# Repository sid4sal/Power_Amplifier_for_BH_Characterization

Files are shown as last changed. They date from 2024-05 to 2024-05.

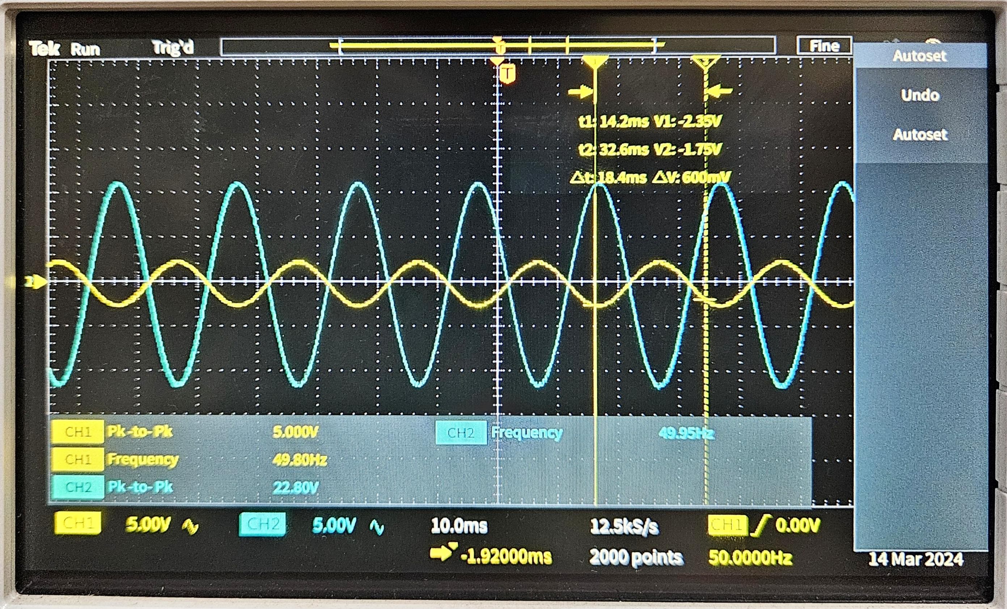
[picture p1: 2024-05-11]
Experiment Results/Vin (ch1) vs Vout (ch2) of the power amplifier.jpeg

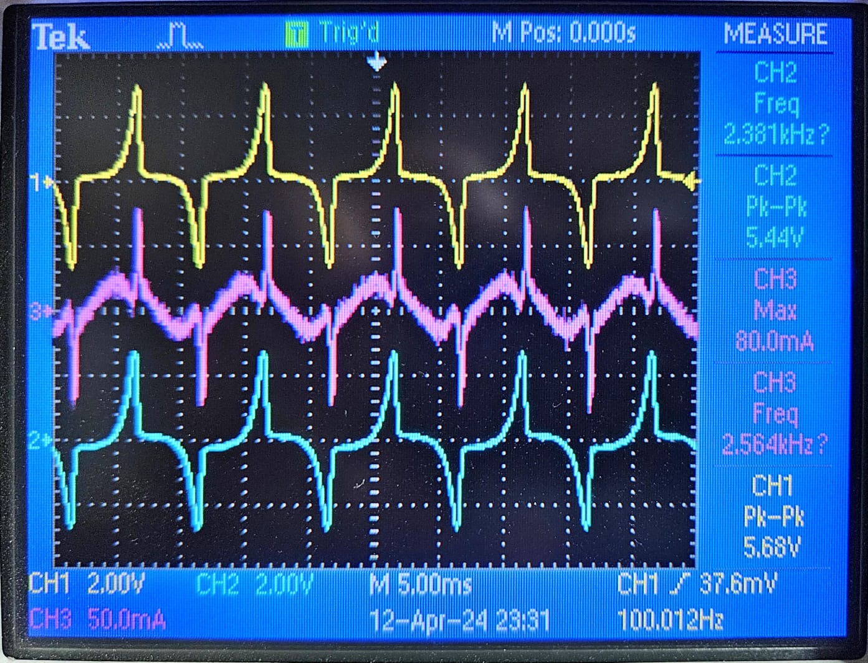
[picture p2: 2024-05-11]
Experiment Results/Primary current (ch3), primary voltage (ch2) and secondary voltage (ch1) at 500hz, 3vpp.jpeg

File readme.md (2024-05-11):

# Design and Implementation of High Bandwidth Power Amplifier for B-H Characterization of Magnetic Materials

## Project Overview

The High Bandwidth Power Amplifier is a device for magnetic materials engineers to obtain B-H characterization of magnetic materials at low as well as high frequencies. It is a transformer-less multi-stage direct-coupled linear power amplifier for the characterization of magnetic cores at various frequencies.

The amplifier operates from 50 Hz to 250 kHz with a gain of approximately 4.6 (13.2 dB). It can handle an input power voltage up to ±60 V, allowing the reference signal to be given up to 12-13 V. The current rating of the amplifier is up to 2.5-3 A (continuous).

The user manual and all the required files can be found at this repo.

## Folder Descriptions

- *B-H_curve_plotting_MatLab*: Contains MATLAB files for plotting the simulated B-H curve of the toroid.
  
- *CAD_Outer_Casing_Design*: Includes the design of the outer casing in JPEG format.
  
- *Circuit_Design_and_simulation_results*: Contains the circuit diagrams, stages, and frequency response simulations in both KiCad and Proteus formats. It also includes the PCB design and 3D view, along with potential improvements.
  
- *Demo_and_Experiment_Videos*: Holds videos demonstrating the initial testing of the breadboard circuit, testing of the amplifier on the toroid core, and PCB testing.
  
- *Experiment Results*: Contains experimental results like B-H characteristic data, observed frequency response with load, and primary and secondary voltages at different frequencies.
  
- *Frequency_Response_Observed_vs_Simulated*: Compares the observed and simulated frequency responses in KiCad and Proteus.
  
- *PCB_Design_and_Circuit_Simulation_KiCad*: Placeholder for the KiCad files related to PCB design and circuit simulation.
  
- *Simulation_Proteus*: Placeholder for the Proteus simulation files.

## Additional Documents

- *Circuit_Diagram.png*: Circuit diagram of the power amplifier.
  
- *PCB.jpeg* & *PCB2.jpeg*: Images of the PCB design.
  
- *Project_Problem_Statement.docx*: Detailed problem statement of the project.
  
- *Toroidal_core_design_and_calculation.pdf*: Design and calculations related to the toroidal core.
  
- *Toroid_Core_Detailed_Calculations.pdf*: Detailed calculations for the toroidal core.
  
- *User Manual for Power Amplifier.pdf*: User manual for operating the power amplifier.

Feel free to reach out to me for any clarifications or further details. my contact details can be found inside the user manual.

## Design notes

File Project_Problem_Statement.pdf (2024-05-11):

# Design and Implementation of High Bandwidth Power Amplifier for B-H Characterization of Magnetic Materials

By

## Siddhesh Sali

(18D070030 - IIT Bombay, Electrical Engineering)

Under Guidance of

## Prof. S V Kulkarni

(Dept. of Electrical Engineering IIT Bombay)

## Prof. Shiladri Chakraborty

(Dept. of Electrical Engineering IIT Bombay)

## Prof. Siddharth Tallur

(Dept. of Electrical Engineering IIT Bombay)

Brief description of what the students are required to build in this project (application, performance requirements and constraints)

The experimental characterization of the magnetic core material at low as well as high frequencies is required as machines and converters operate at a wide range of frequencies. For this, power amplifiers having wide bandwidth, high voltage, and current gains, along with low output offset are needed. In this project, students will build high-bandwidth voltage and current amplifiers for B-H characterization of magnetic materials. The setup will look similar to the one shown in Ref 1.

Key technical and user specifications

The designed power amplifier should be capable of characterizing a ferrite core material using the ring-specimen method up to a peak flux density of 0.3 T for a wide frequency range from 50 Hz to 10 kHz.

Deliverable expected

A review of conventional topologies and the new amplifier design should be given. The experimental results of the proposed voltage and current amplifiers and the closed-loop power amplifier need to be presented. Experimental waveforms of secondary induced voltage, core flux-linkage, and primary coil current should be shown. The students should give inputs to extend the frequency range from 10 kHz to 50 kHz.

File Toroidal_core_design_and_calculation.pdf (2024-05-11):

### 2024 date

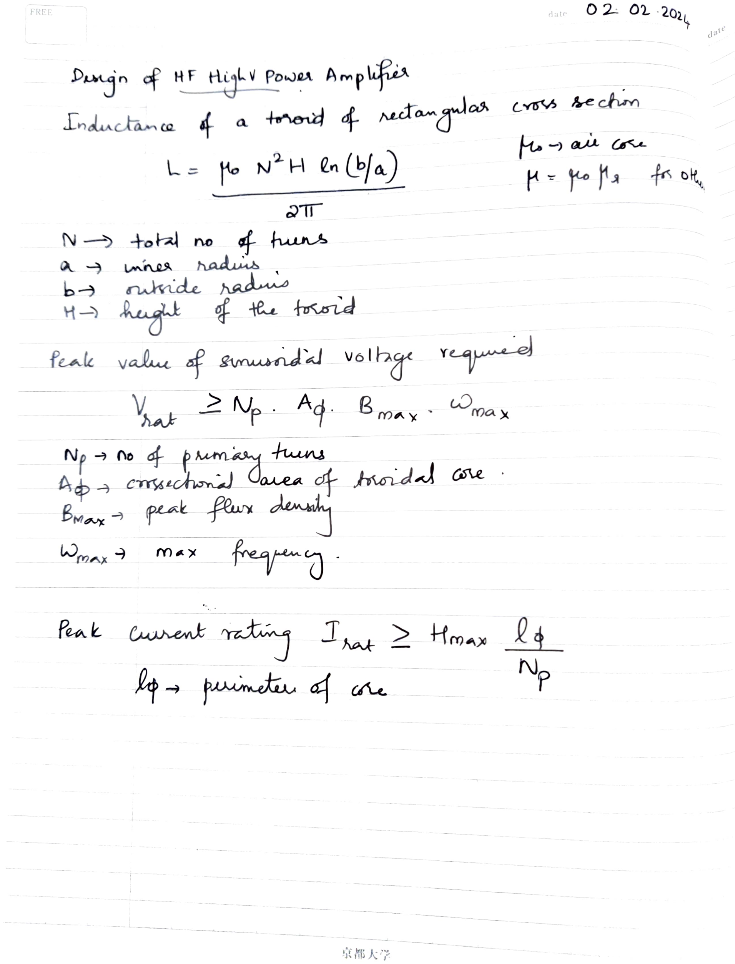
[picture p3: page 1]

FREE
PoJea Amplfhes
Inductama 4 a tohod ¢ etamga

Ntotal no

b’

Le fo NH en (b/a)

Buas

nnes hadis
ride hadis

feak vale f sinndad volage

cnsechnl

max

Peak Crent

Ad. Bmay
tuns

Boav Wa

reqe

date

CYoS bechn

### dependng on aailaki liy

## (A vailaLe at eementl4)

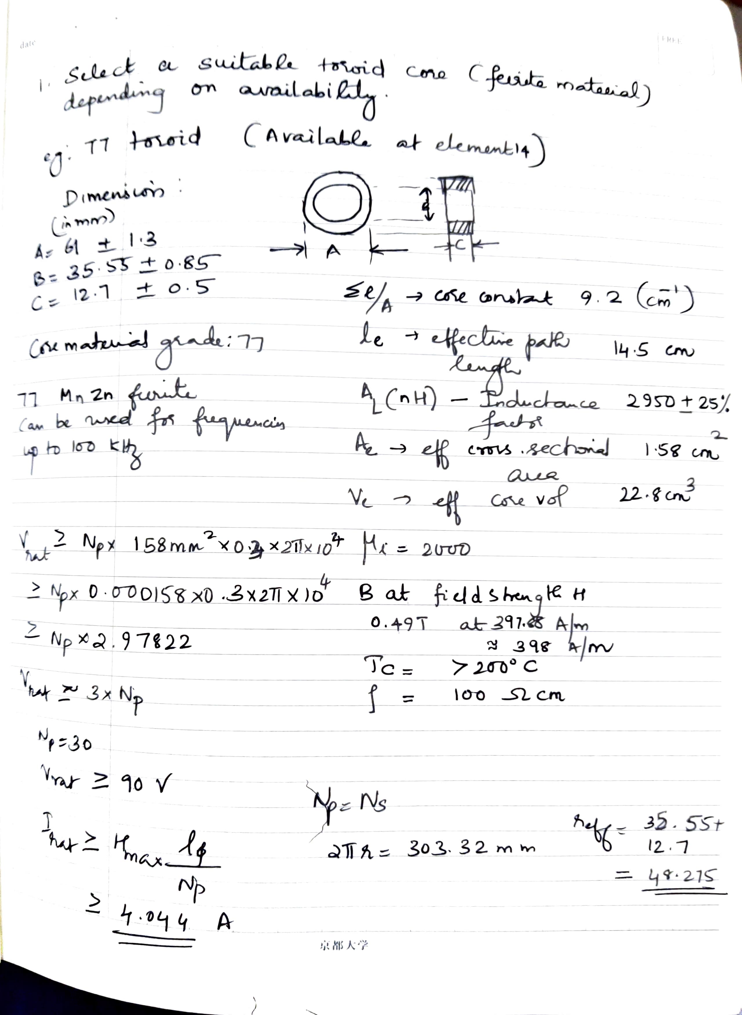
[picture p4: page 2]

date

1: T7 toroid

Dimenin
(à mm)
A 6 + l3
B: 35 S3 to-85

t

71 Mn 2n fit

2 Np xa.9 7622

30

4.o4 4 A

A
S’ cse outat 9.2 (cm')

A

Ve
158 mmxox21x 10T = 200D

’

## Cfeita tasil)

0.49T
f

CUS Bechi

B at fddshenge H

Cse vof

at 297.8 Afon

|o0 | S cm
1A | 303. 32 m m

2950t 25,

2

35. 55t
I2.7

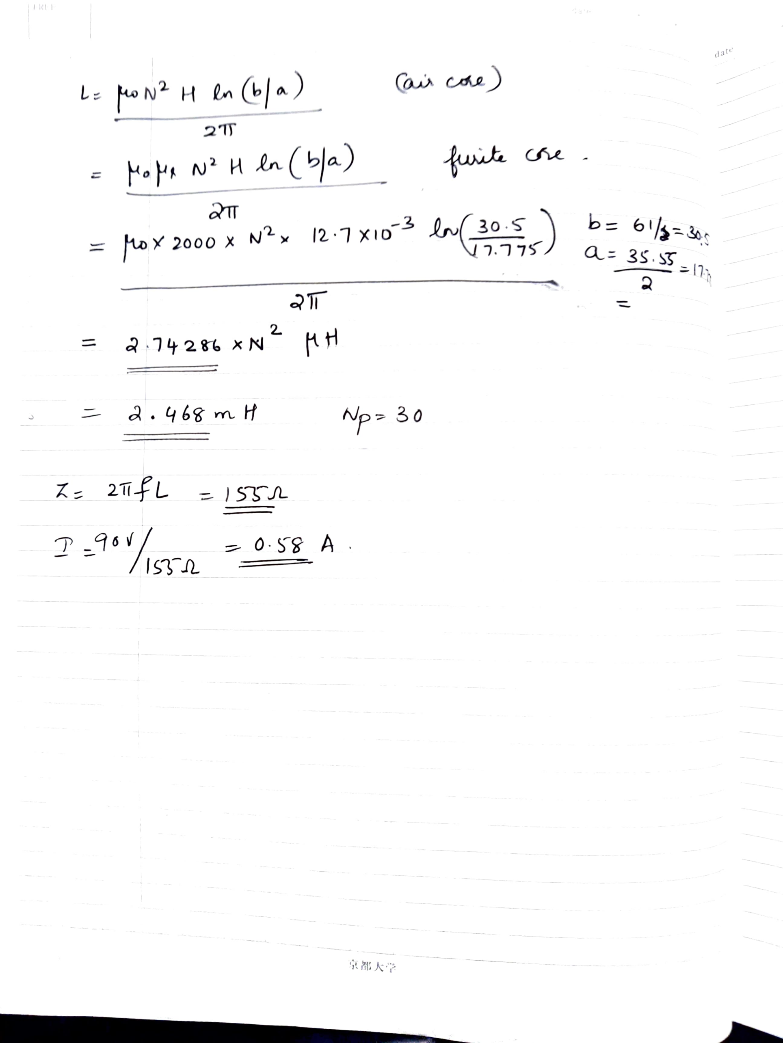
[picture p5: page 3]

Le hoN H ln

21)

= ox 2000 X N?

a. 468 m H

/a)

2

Cais cae)

2-1x103 la30s b= 6'

0.SS A

30

az 3S.SS.

date'

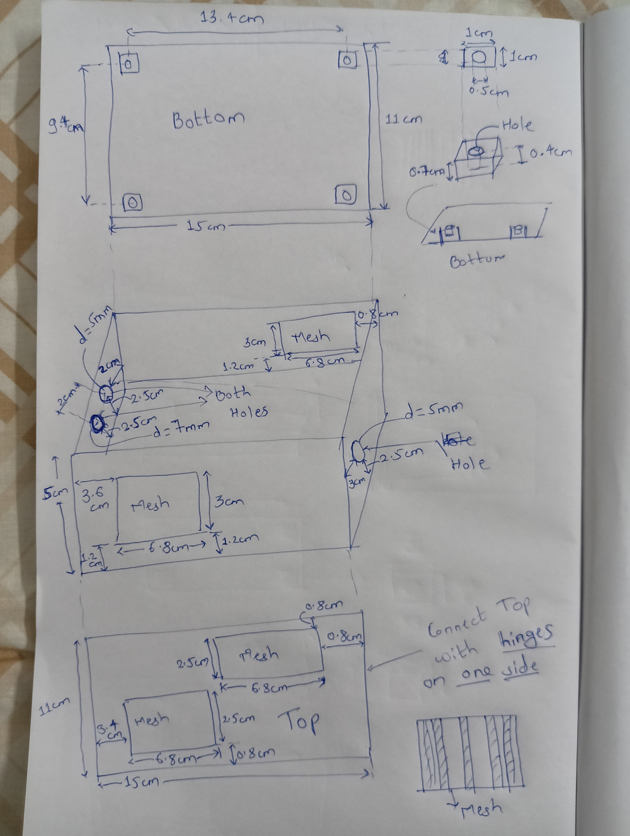
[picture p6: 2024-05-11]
CAD_Outer_Casing_Design/Outer_Casing.jpeg

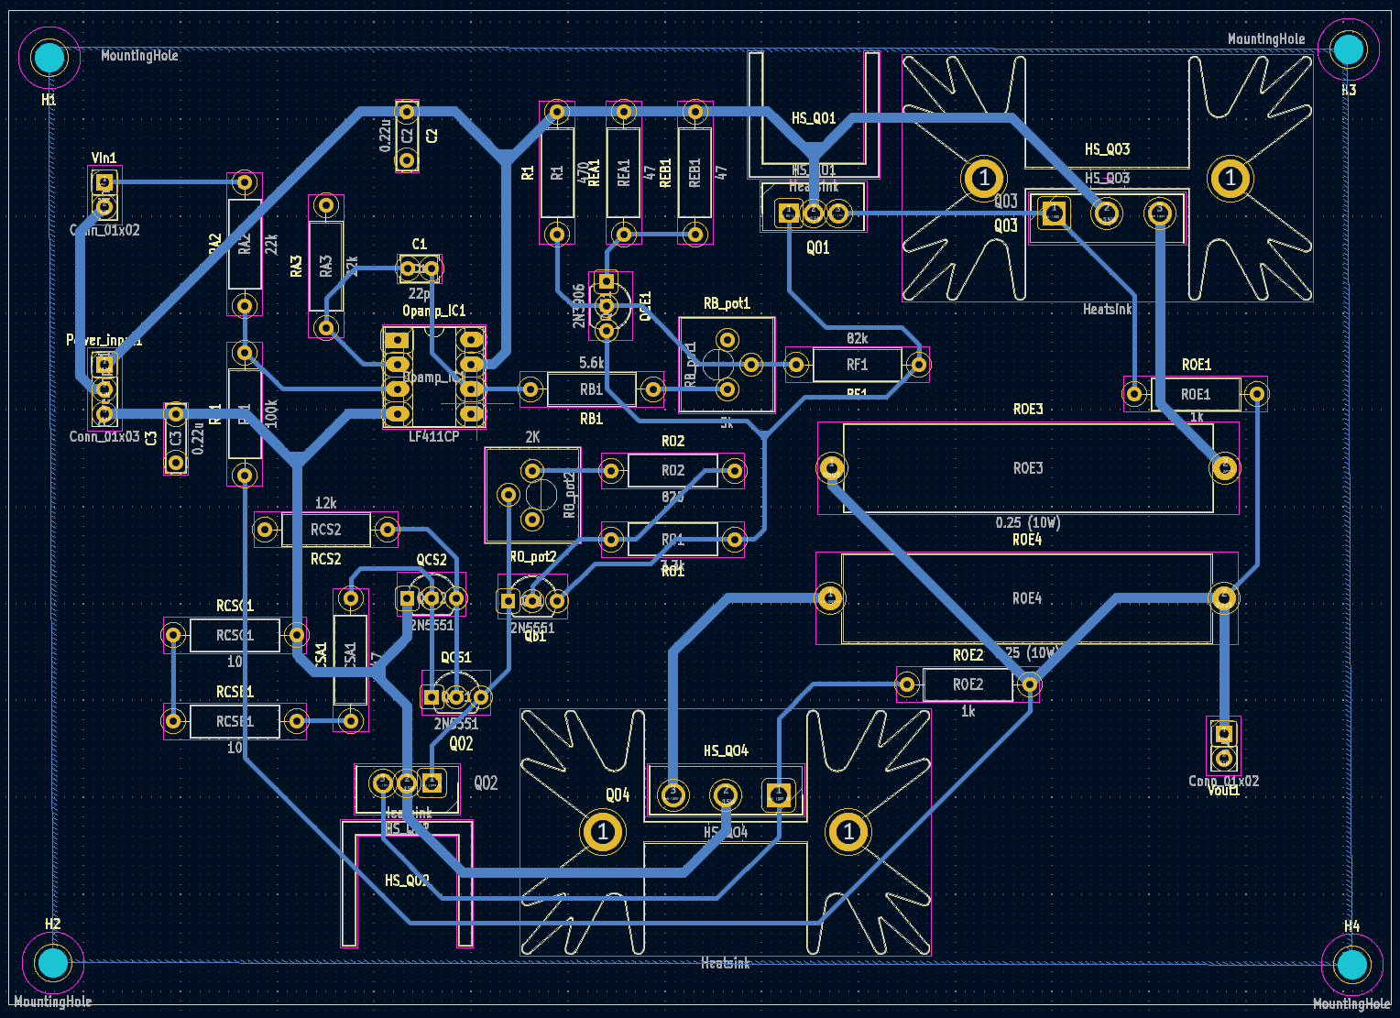
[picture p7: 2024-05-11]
Circuit_Design_and_simulation_results/PCB_Design.png

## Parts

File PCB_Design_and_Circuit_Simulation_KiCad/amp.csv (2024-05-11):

Source: | C:\Users\siddh\Desktop\IITB_23-24_spring\EE 344 Electronic Design Lab\Project-p17\circuit_and_pcb\amp\amp.kicad_sch
Date: | 19-03-2024 15:52
Tool: | Eeschema 7.0.10
Generator: | C:\Program Files\KiCad\7.0\bin\scripting\plugins/bom_csv_grouped_by_value.py
Component Count: | 30
Collated Components:
Item | Qty | Reference(s) | Value | LibPart | Footprint | Datasheet | DNP | Height | Manufacturer_Name | Manufacturer_Part_Number | Mouser Part Number | Mouser Price/Stock | Sim.Enable
1 | 1 | C1 | 22p | Device:C | Capacitor_THT:C_Disc_D3.8mm_W2.6mm_P2.50mm | ~
2 | 1 | Opamp_IC1 | LF411CP | SamacSys_Parts:LF411CP | SamacSys_Parts:DIP794W53P254L959H508Q8N | http://www.ti.com/lit/ds/symlink/lf411.pdf |  | 5.08 | Texas Instruments | LF411CP | 595-LF411CP | https://www.mouser.co.uk/ProductDetail/Texas-Instruments/LF411CP?qs=JS6RUWRH9DWau2Mor%2F%252BoLg%3D%3D
3 | 1 | Power_input1 | Conn_01x03 | Connector_Generic:Conn_01x03 | Connector_PinHeader_2.54mm:PinHeader_1x03_P2.54mm_Vertical | ~
4 | 3 | Qb1, QCS1, QCS2 | 2N5551 | SamacSys_Parts:2N5551 | Package_TO_SOT_THT:TO-92L_Inline_Wide | http://www.onsemi.com/pub/Collateral/2N5550-D.PDF |  | 5.33 | onsemi | 2N5551 | 863-2N5551 | https://www.mouser.co.uk/ProductDetail/onsemi/2N5551?qs=vLkC5FC1VN9fmjXMZdtXVg%3D%3D
5 | 1 | QCE1 | 2N3906 | Transistor_BJT:2N3906 | Package_TO_SOT_THT:TO-92L_Inline_Wide | https://www.onsemi.com/pub/Collateral/2N3906-D.PDF |  |  |  |  |  |  | 0
6 | 1 | QO1 | MJE15034G | SamacSys_Parts:MJE15034G | SamacSys_Parts:TO254P483X1010X2035-3P | http://www.onsemi.com/pub/Collateral/MJE15034-D.PDF |  | 4.83 | onsemi | MJE15034G | 863-MJE15034G | https://www.mouser.co.uk/ProductDetail/onsemi/MJE15034G?qs=HVbQlW5zcXV7QTziNO9oMQ%3D%3D
7 | 1 | QO2 | MJE15035G | SamacSys_Parts:MJE15035G | SamacSys_Parts:TO254P483X1010X2035-3P | http://www.onsemi.com/pub/Collateral/MJE15034-D.PDF |  | 4.83 | onsemi | MJE15035G | 863-MJE15035G | https://www.mouser.co.uk/ProductDetail/onsemi/MJE15035G?qs=HVbQlW5zcXXa%252Byhv1vIoqQ%3D%3D
8 | 1 | QO3 | NJW3281G | SamacSys_Parts:NJW3281G | SamacSys_Parts:TO545P500X1560X2380-3P | https://www.onsemi.com/pub/Collateral/NJW3281-D.PDF |  | 5 | onsemi | NJW3281G | 863-NJW3281G | https://www.mouser.co.uk/ProductDetail/onsemi/NJW3281G?qs=WOJDpfhxrCaDJlemeW6i8g%3D%3D
9 | 1 | QO4 | NJW1302G | SamacSys_Parts:NJW1302G | SamacSys_Parts:TO545P500X1560X2380-3P | http://www.onsemi.com/pub/Collateral/NJW3281-D.PDF |  | 5 | onsemi | NJW1302G | 863-NJW1302G | https://www.mouser.co.uk/ProductDetail/onsemi/NJW1302G?qs=WOJDpfhxrCZWcBqHAA%2FzUg%3D%3D
10 | 1 | R1 | 470 | Device:R | Resistor_THT:R_Axial_DIN0309_L9.0mm_D3.2mm_P12.70mm_Horizontal | ~
11 | 1 | RA1 | 100k | Device:R | Resistor_THT:R_Axial_DIN0309_L9.0mm_D3.2mm_P12.70mm_Horizontal | ~
12 | 2 | RA2, RA3 | 22k | Device:R | Resistor_THT:R_Axial_DIN0309_L9.0mm_D3.2mm_P12.70mm_Horizontal | ~
13 | 1 | RB1 | 5.6k | Device:R | Resistor_THT:R_Axial_DIN0309_L9.0mm_D3.2mm_P12.70mm_Horizontal | ~
14 | 1 | RB_pot1 | 5k | Device:R_Potentiometer | Potentiometer_THT:Potentiometer_Bourns_3386P_Vertical | ~
15 | 1 | RCS1 | 68 | Device:R | Resistor_THT:R_Axial_DIN0309_L9.0mm_D3.2mm_P12.70mm_Horizontal | ~ | 47+10+10
16 | 1 | RCS2 | 12k | Device:R | Resistor_THT:R_Axial_DIN0309_L9.0mm_D3.2mm_P12.70mm_Horizontal | ~
17 | 1 | RE1 | 22 | Device:R | Resistor_THT:R_Axial_DIN0309_L9.0mm_D3.2mm_P12.70mm_Horizontal | ~ | 47||47
18 | 1 | RF1 | 82k | Device:R | Resistor_THT:R_Axial_DIN0309_L9.0mm_D3.2mm_P12.70mm_Horizontal | ~
19 | 1 | RO1 | 3.3k | Device:R | Resistor_THT:R_Axial_DIN0309_L9.0mm_D3.2mm_P12.70mm_Horizontal | ~
20 | 1 | RO2 | 820 | Device:R | Resistor_THT:R_Axial_DIN0309_L9.0mm_D3.2mm_P12.70mm_Horizontal | ~
21 | 1 | RO_pot2 | 2K | Device:R_Potentiometer | Potentiometer_THT:Potentiometer_Bourns_3386P_Vertical | ~ | 5k pot
22 | 4 | ROE1, ROE2, ROE3, ROE4 | 1k | Device:R | Resistor_THT:R_Axial_DIN0309_L9.0mm_D3.2mm_P12.70mm_Horizontal | ~
23 | 2 | Vin1, Vout1 | Conn_01x02 | Connector_Generic:Conn_01x02 | Connector_PinHeader_2.54mm:PinHeader_1x02_P2.54mm_Vertical | ~

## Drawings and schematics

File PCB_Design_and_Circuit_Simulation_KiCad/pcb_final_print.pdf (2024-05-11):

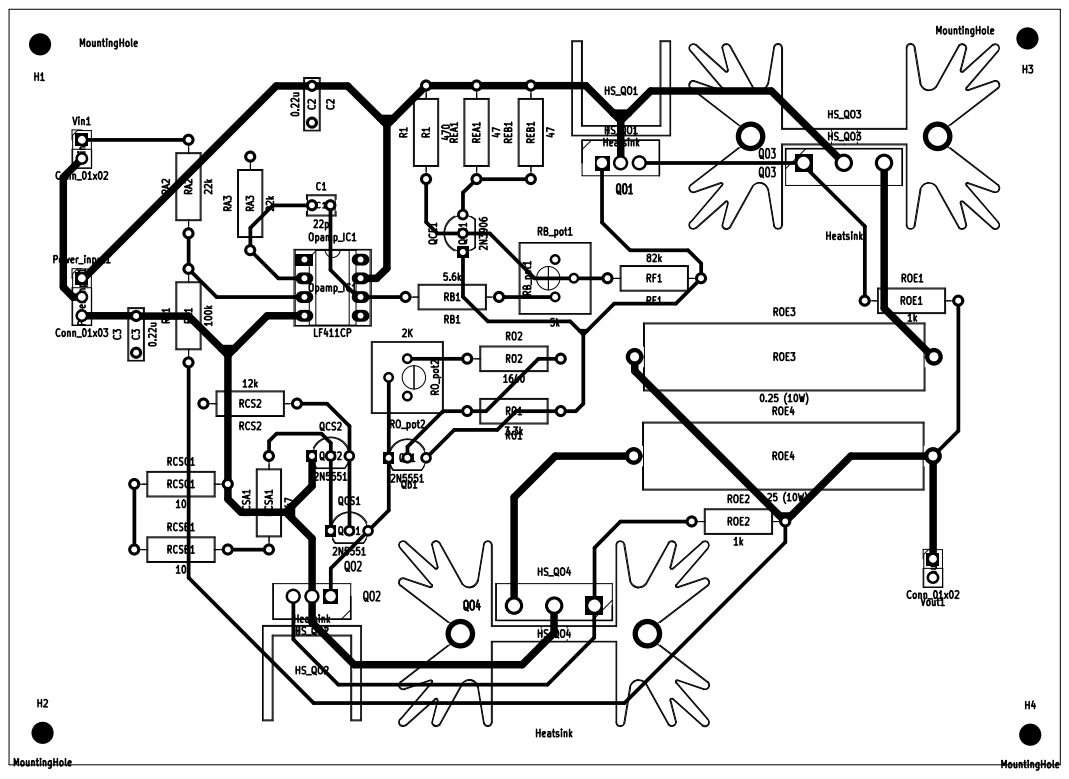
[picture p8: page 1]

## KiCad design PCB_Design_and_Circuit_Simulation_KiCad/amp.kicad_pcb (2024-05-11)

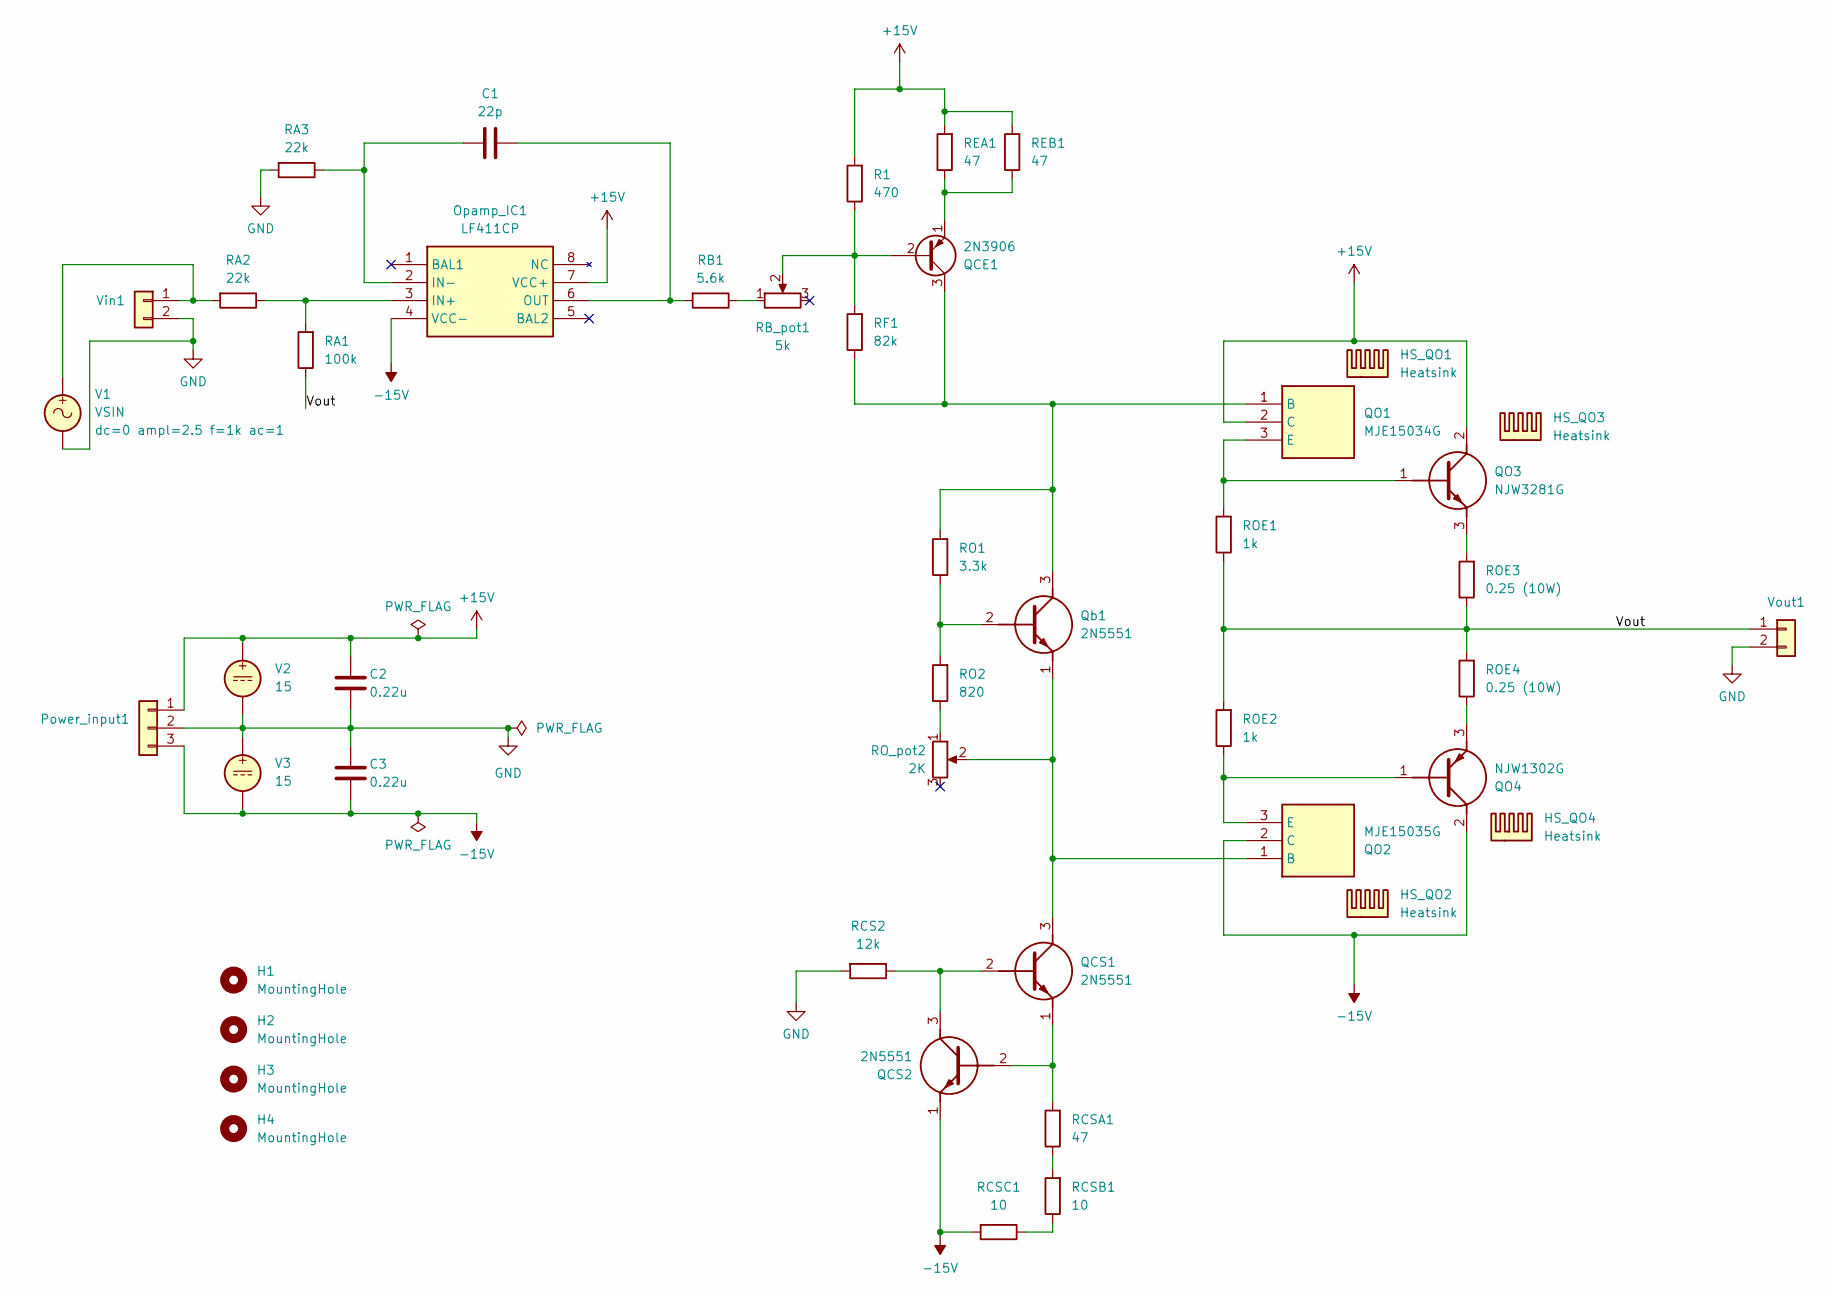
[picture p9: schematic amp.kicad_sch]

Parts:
C1: 22p; C_Disc_D3.8mm_W2.6mm_P2.50mm
C2, C3: 0.22u; C_Rect_L7.0mm_W2.0mm_P5.00mm
H1, H2, H3, H4: MountingHole; MountingHole_3mm
HS_QO1, HS_QO2: Heatsink; Heatsink_Stonecold_HS-S03_13.21x12.7mm
HS_QO3, HS_QO4: Heatsink; Heatsink_Fischer_SK129-STS_42x25mm_2xDrill2.5mm
Opamp_IC1: LF411CP; DIP-8_W7.62mm_Socket_LongPads; Mouser Part Number 595-LF411CP
Power_input1: Conn_01x03; PinHeader_1x03_P2.54mm_Vertical
QCE1: 2N3906; TO-92L_Inline_Wide
QCS1, QCS2: 2N5551; TO-92L_Inline_Wide; Mouser Part Number 863-2N5551
QO1: MJE15034G; TO254P483X1010X2035-3P; Mouser Part Number 863-MJE15034G
QO2: MJE15035G; TO254P483X1010X2035-3P; Mouser Part Number 863-MJE15035G
QO3: NJW3281G; TO545P500X1560X2380-3P; Mouser Part Number 863-NJW3281G
QO4: NJW1302G; TO545P500X1560X2380-3P; Mouser Part Number 863-NJW1302G
Qb1: 2N5551; TO-92L_Inline_Wide; Mouser Part Number 863-2N5551
R1: 470; R_Axial_DIN0309_L9.0mm_D3.2mm_P12.70mm_Horizontal
RA1: 100k; R_Axial_DIN0309_L9.0mm_D3.2mm_P12.70mm_Horizontal
RA2, RA3: 22k; R_Axial_DIN0309_L9.0mm_D3.2mm_P12.70mm_Horizontal
RB1: 5.6k; R_Axial_DIN0309_L9.0mm_D3.2mm_P12.70mm_Horizontal
RB_pot1: 5k; Potentiometer_Bourns_3386P_Vertical
RCS2: 12k; R_Axial_DIN0309_L9.0mm_D3.2mm_P12.70mm_Horizontal
RCSA1: 47; R_Axial_DIN0309_L9.0mm_D3.2mm_P12.70mm_Horizontal
RCSB1: 10; R_Axial_DIN0309_L9.0mm_D3.2mm_P12.70mm_Horizontal
RCSC1: 10; R_Axial_DIN0309_L9.0mm_D3.2mm_P12.70mm_Horizontal
REA1: 47; R_Axial_DIN0309_L9.0mm_D3.2mm_P12.70mm_Horizontal
REB1: 47; R_Axial_DIN0309_L9.0mm_D3.2mm_P12.70mm_Horizontal
RF1: 82k; R_Axial_DIN0309_L9.0mm_D3.2mm_P12.70mm_Horizontal
RO1: 3.3k; R_Axial_DIN0309_L9.0mm_D3.2mm_P12.70mm_Horizontal
RO2: 820; R_Axial_DIN0309_L9.0mm_D3.2mm_P12.70mm_Horizontal
ROE1, ROE2: 1k; R_Axial_DIN0309_L9.0mm_D3.2mm_P12.70mm_Horizontal
ROE3, ROE4: 0.25 (10W); R_Axial_Power_L38.0mm_W9.0mm_P40.64mm
RO_pot2: 2K; Potentiometer_Bourns_3386P_Vertical
V1: VSIN
V2, V3: 15
Vin1: Conn_01x02; PinHeader_1x02_P2.54mm_Vertical
Vout1: Conn_01x02; PinHeader_1x02_P2.54mm_Vertical

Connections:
+15V: C2.1, Opamp_IC1.7 (VCC+), Power_input1.1, QO1.2 (C), QO3.2 (C), R1.2, REA1.2, REB1.2, V2.1
-15V: C3.2, Opamp_IC1.4 (VCC-), Power_input1.3, QCS2.1 (E), QO2.2 (C), QO4.2 (C), RCSC1.2, V3.2
/Vout: RA1.1, ROE1.1, ROE2.2, ROE3.1, ROE4.2, Vout1.1
GND: C2.2, C3.1, Power_input1.2, RA3.2, RCS2.2, V1.2, V2.2, V3.1, Vin1.2, Vout1.2
unnamed: Opamp_IC1.3 (IN+), RA1.2, RA2.1
unnamed: C1.1, Opamp_IC1.2 (IN-), RA3.1
unnamed: C1.2, Opamp_IC1.6 (OUT), RB1.2
unnamed: QCE1.2 (B), R1.1, RB_pot1.2, RF1.2
unnamed: QCE1.3 (C), QO1.1 (B), Qb1.3 (C), RF1.1, RO1.2
unnamed: QCE1.1 (E), REA1.1, REB1.1
unnamed: QCS1.2 (B), QCS2.3 (C), RCS2.1
unnamed: QCS1.3 (C), QO2.1 (B), Qb1.1 (E), RO_pot2.2
unnamed: QCS1.1 (E), QCS2.2 (B), RCSA1.2
unnamed: QO1.3 (E), QO3.1 (B), ROE1.2
unnamed: QO2.3 (E), QO4.1 (B), ROE2.1
unnamed: QO3.3 (E), ROE3.2
unnamed: QO4.3 (E), ROE4.1
unnamed: Qb1.2 (B), RO1.1, RO2.2
unnamed: RB1.1, RB_pot1.1
unnamed: RCSA1.1, RCSB1.2
unnamed: RCSB1.1, RCSC1.1
unnamed: RO2.1, RO_pot2.1
unnamed: RA2.2, V1.1, Vin1.1

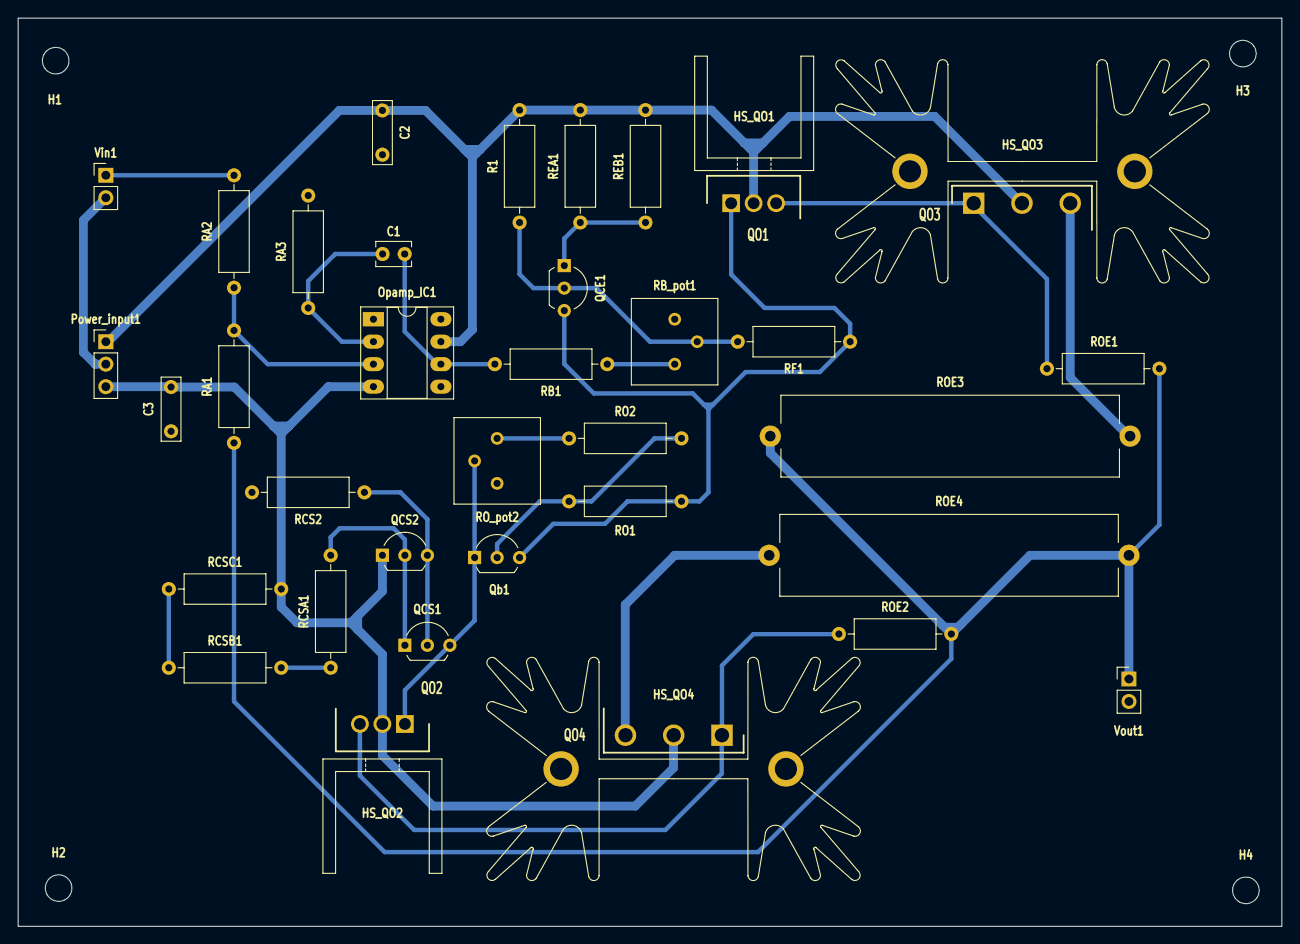
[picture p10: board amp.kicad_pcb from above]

Board: 2 copper layers, 142.7 x 102.6 mm, 43 parts (0 on the bottom side), 23 nets.

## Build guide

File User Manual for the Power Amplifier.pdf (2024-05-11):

# USER MANUAL

# HIGH BANDWIDTH POWER AMPLIFIER

The amplifier possesses a voltage gain of 4.6 (13.2 dB)

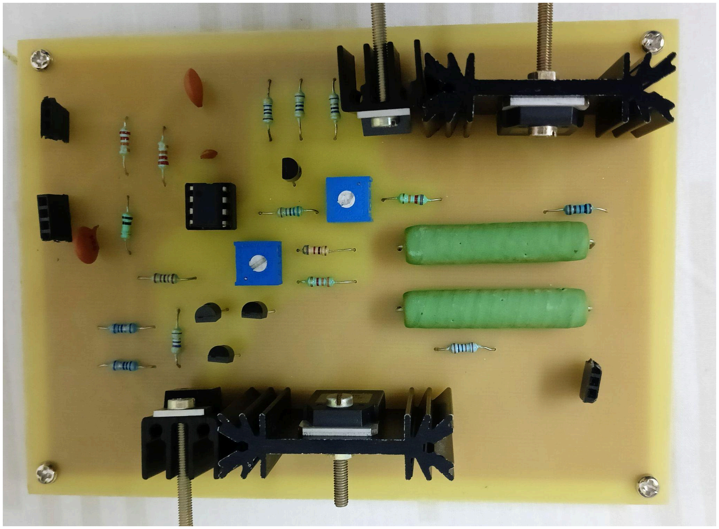
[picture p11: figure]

BY

## Siddhesh Sali

siddhesh@sids.fun

(IIT Bombay, Electrical Engineering)

## INTRODUCTION

The High Bandwidth Power Amplifier is a device for magnetic materials engineers to obtain B-H characterization of magnetic materials at low as well as high frequencies. This is a transformer-less multi-stage direct-coupled linear power amplifier for the characterization of magnetic cores at various frequencies.

This document is the user manual of the multistage direct-coupled linear power amplifier for the characterization of magnetic cores at wide frequency range.

## TECHNICAL SPECIFICATIONS

➔ Voltage Gain: 4.6 (13.2 dB)
➔ Rated voltage/Max Power Input Voltage: ±60 V ➔ Rated current: 3 A
➔ Frequency range: 50 Hz to 250 kHz
➔ Max Input Signal Voltage: 13V
➔ Max safe power dissipation for driver BJTs (MJE15034 and MJE15035) : 2 W ➔ Max safe power dissipation for main BJTs (NJW3281 and NJW1302) : 3.125 W

The amplifier is designed to operate from 50 Hz to 250 kHz and is intended for experimental B-H characterizations of ferrite cores. The gain of the amplifier is approximately 4.6 (13.2 dB). The input power voltage can be increased up to ±60 V, hence the input (reference) signal can be given up to 12-13 V. The current rating of this amplifier is up to 2.5 to 3 A.

## OPERATING INSTRUCTIONS

To operate the amplifier follow these steps (also refer to the following images):

1. Powering on the amplifier:
- Ensure that the power supply is set to less than rated voltage and also ensure that it is turned off before connecting the amplifier.
- Connect the power supply to the Power Input port of the amplifier.
- Turn on the power supply.
2. Setting input signals:

1

- Connect the input signal source to the Reference/Input Signal (Vin) port on the amplifier.
- Adjust the input signal level based on the requirements of the experiment or test.
- Use the AFG to vary the frequency accordingly.
3. Caution:
- To get the desired results, always calculate your load characteristics and ensure that the current flowing through the load at any point in time is below 3A.

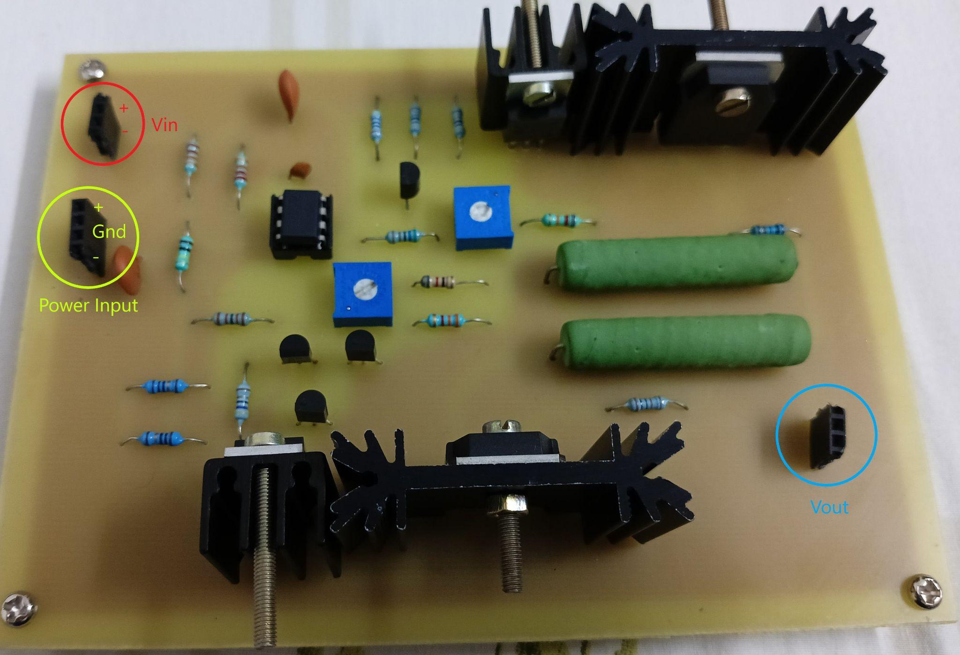
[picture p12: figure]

### Ports on the PCB

2

## TROUBLESHOOTING

- If the output waveform is deformed and the frequency is within the rated value then it might be the case that the output is saturated. Hence check if the {max voltage of the input signal} * {Amplifier Gain (4.6)} is less than the voltage applied to the power input.
- When working with the toroid core if the DCR of the toroid is very low it will draw very large current and may damage the amplifier or the power supply. When a load with very low DCR is connected, the power supply may act as if it is shorted. To solve this problem, always ensure that the current is within the rated limit of the power supply by connecting a resistor in series with the load/toroid. Choose the value of the resistor as low as possible while making sure that the current is just below rated value. This is so that the voltage across the toroid core remains high for the low frequencies also and it will enable us to measure the b-h characteristics at low frequencies too.

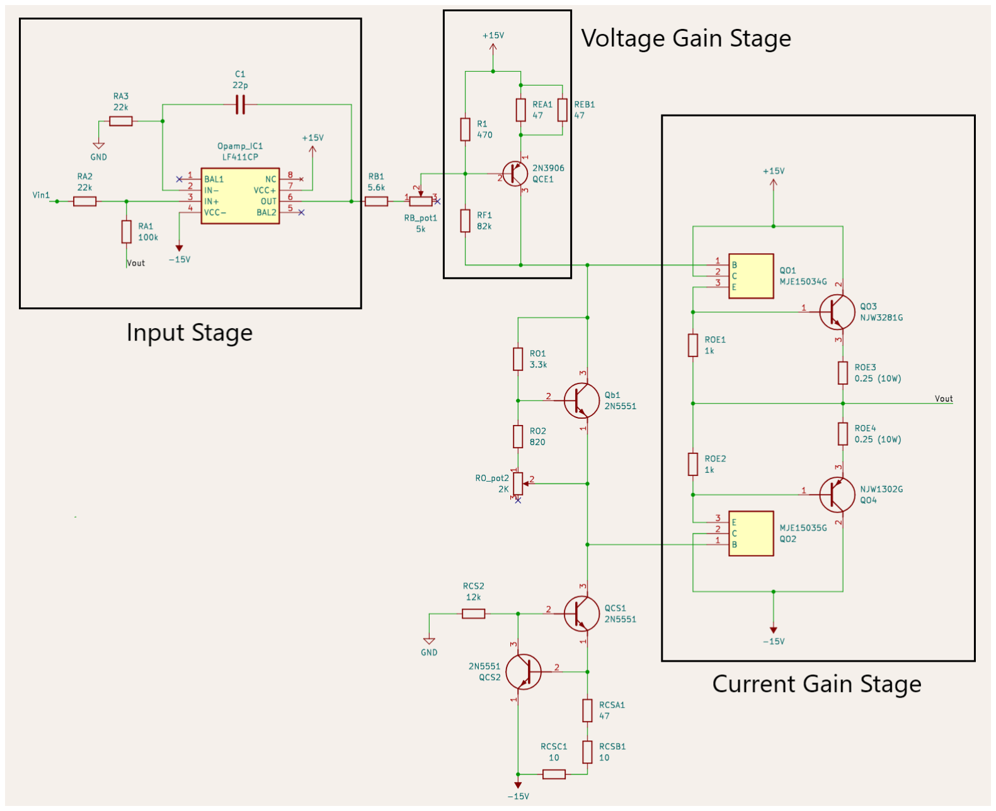
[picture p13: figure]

Circuit Diagram

3

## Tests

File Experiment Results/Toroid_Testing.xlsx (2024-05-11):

Vin (Vpp) | Primary Voltage (Vpp) | Secondry Voltage (Vpp) | Primary Current (A)
0.1 | 0.44 | 0.52 | 0.017
0.2 | 0.96 | 1 | 0.02
0.3 | 1.44 | 1.56 | 0.0224
0.4 | 1.96 | 2.02 | 0.0256
0.5 | 2.32 | 2.56 | 0.0272
0.6 | 2.72 | 2.92 | 0.0304
0.7 | 3.36 | 3.36 | 0.032
0.8 | 3.72 | 3.76 | 0.0344
0.9 | 4.24 | 4.16 | 0.0352
1 | 4.4 | 4.72 | 0.0384
1.1 | 4.88 | 5.12 | 0.0384
1.2 | 5.44 | 5.44 | 0.0424
1.3 | 5.76 | 5.84 | 0.0464
1.4 | 6.08 | 6.16 | 0.0496
1.5 | 6.56 | 6.61 | 0.0528
1.6 | 6.88 | 7.12 | 0.0576
1.7 | 7.28 | 7.44 | 0.0576
1.8 | 8 | 8.2 | 0.0608
1.9 | 8.6 | 8.8 | 0.0648
2 | 8.8 | 9.2 | 0.0688
2.1 | 9.4 | 9.6 | 0.0744
2.2 | 9.8 | 10.2 | 0.0784
2.3 | 10.2 | 10.6 | 0.084
2.4 | 10.4 | 11 | 0.092
2.5 | 10.6 | 11.4 | 0.0968
2.6 | 11.4 | 11.8 | 0.102
2.7 | 11.8 | 12.2 | 0.107
2.8 | 12.2 | 12.6 | 0.114
2.9 | 12.6 | 13 | 0.126
3 | 13 | 13.4 | 0.134

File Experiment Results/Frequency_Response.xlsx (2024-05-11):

Vin = 5Vpp
V_in (Vpp) | Input_freq | V_out (Vpp) | Output_freq | Gain | phase diff
5 | 50 | 22.6 | 50 | 4.52 | 173
5 | 100 | 22.8 | 100 | 4.56 | 176
5 | 500 | 23 | 500 | 4.6 | 180
5 | 1k | 23 | 1000 | 4.6 | 179
5 | 2k | 23 | 2000 | 4.6 | 180
5 | 3k | 23 | 3000 | 4.6 | 179
5 | 4k | 23 | 4000 | 4.6 | 179
5 | 5k | 23 | 5000 | 4.6 | 178
5 | 6k | 23 | 6000 | 4.6 | 179
5 | 7k | 23 | 7000 | 4.6 | 178
5 | 8k | 23 | 8000 | 4.6 | 178
5 | 9k | 23.2 | 9000 | 4.64 | 177
5 | 10k | 23.2 | 10000 | 4.64 | 178
5 | 20k | 23.4 | 20000 | 4.68 | 175
5 | 30k | 23 | 30000 | 4.6 | 176
5 | 40k | 23 | 40000 | 4.6 | 170
5 | 50k | 23 | 50000 | 4.6 | 177

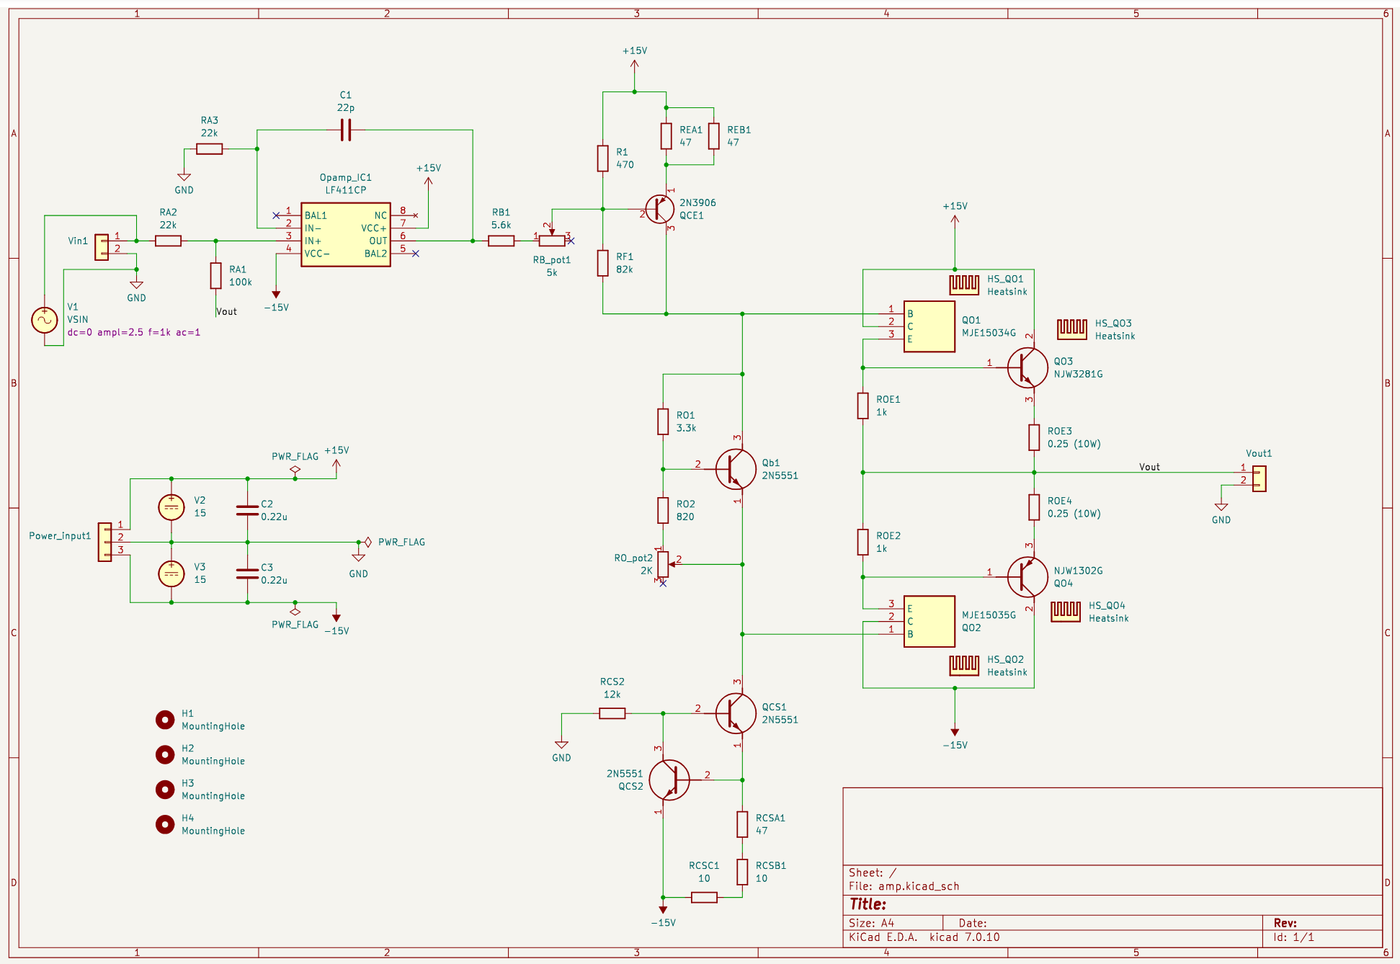
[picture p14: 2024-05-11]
Circuit_Design_and_simulation_results/Circuit_Final_Diagram.png

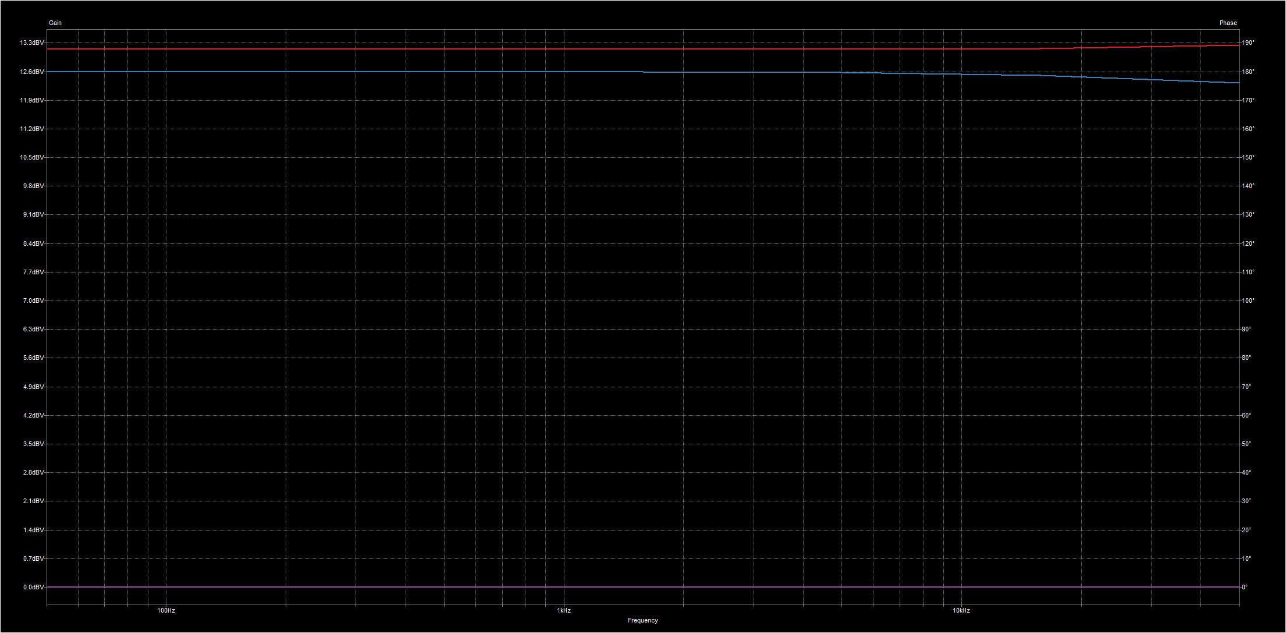
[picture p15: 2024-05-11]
Circuit_Design_and_simulation_results/Frequency_Response_simulated_KiCad.png
